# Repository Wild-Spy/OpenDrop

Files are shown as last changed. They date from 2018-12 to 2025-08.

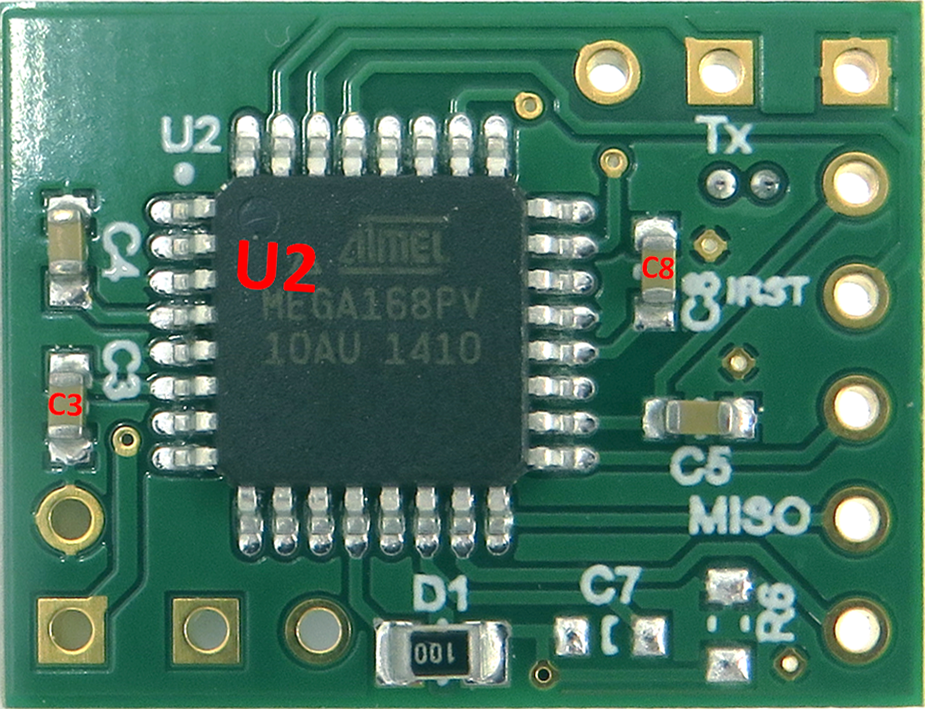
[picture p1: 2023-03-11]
Production/NichDrop Board V0.2 Production Files/Assisted Assembly Files/OpenDrop_PCB_Back.png

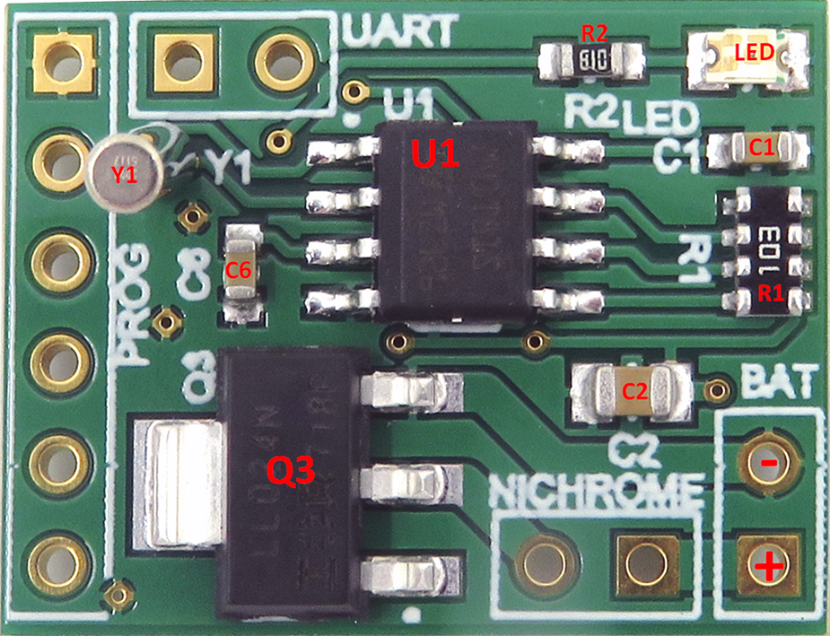
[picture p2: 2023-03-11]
Production/NichDrop Board V0.2 Production Files/Assisted Assembly Files/OpenDrop_PCB_Front.png

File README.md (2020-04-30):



# OpenDrop
OpenDrop is an open source, low cost drop-off unit for animal-borne devices. Provided herein is code for device firmware and programming software (Windows binaries available under [Releases](https://github.com/Wild-Spy/OpenDrop/releases)). Additionally, Gerber files for PCB fabrication and CAD files for a small/medium mammal housing mould master are included.

## Requirements
Device firmware is written in C and requires the AVR/Atmel Studio IDE - https://www.microchip.com/mplab/avr-support/avr-and-sam-downloads-archive

Programming software is written in Visual Basic and requires the Microsoft Visual Studio IDE - https://visualstudio.microsoft.com

## Further Information
A more detailed overview of OpenDrop and its use in wildlife biology is covered in: 

Rafiq, K., Appleby, R.G., Edgar, J.P., Jordan, N.R., Dexter, C.E., Jones, D.N., Blacker, A.R.F., and Cochrane, M. 2019, 'OpenDrop: An open-source, low-cost drop-off unit for animal borne devices', *Methods in Ecology and Evolution*, **10**, pp. 1517– 1522. https://doi.org/10.1111/2041-210X.13231

## License
This project is licensed under the terms of the GNU General Public License v3.0. See [LICENSE](LICENSE) for details.

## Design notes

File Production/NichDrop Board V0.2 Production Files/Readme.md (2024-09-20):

| Layer                	|  Filename             	|
|----------------------	|------------------------	|
| Top Copper          	|  NichromeDrop_V2R0.GTL 	|
| Top Solder Mask     	|  NichromeDrop_V2R0.GTS 	|
| Top Silk Screen     	|  NichromeDrop_V2R0.GTO 	|
| Bottom Copper       	|  NichromeDrop_V2R0.GBL 	|
| Bottom Solder Mask  	|  NichromeDrop_V2R0.GBS 	|
| Bottom Silk Screen  	|  NichromeDrop_V2R0.GBO 	|
| Board Outline       	|  NichromeDrop_V2R0.GKO 	|
| Top Solder Paste     	|  NichromeDrop_V2R0.GTP 	|
| Bottom Solder Paste  	|  NichromeDrop_V2R0.GBP 	|
| Excellon Drill File   |  NichromeDrop_V2R0.TXT 	|

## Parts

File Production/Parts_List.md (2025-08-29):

| **Designator** | **Side<sup>§</sup>** | **Size** | **Part**    | **Value** | **OI<sup>†</sup>** |
|:--------------:|:---------:|:--------:|:-----------:|:---------:|:-------:|
| U1             | Front     | ----     | ----        | M41T81S   | Yes     |
| R1             | Front     | ----     | ----        | 4xResNet  | No      |
| Q3             | Front     | SOT223   | MOSFET      | IRLL024N  | Yes     |
| C1             | Front     | 603      | Cap         | 0.1uF     | No      |
| C2             | Front     | 805      | Cap         | 47uF      | No      |
| C6             | Front     | 603      | Cap         | 0.1uF     | No      |
| R2             | Front     | 603      | Resistor    | 1kOhm     | No      |
| LED            | Front     | 805      | LED         | Red       | Yes     |
| Y1             | Front     | Can      | Xtal        | 32768Hz   | No      |
|                |           |          |             |           |         |
| U2             | Back      | ----     | ATMEGA168PV | ----      | Yes     |
| D1             | Back      | 0805     | Resistor    | 100hm     | No      |
| C3             | Back      | 0603     | Cap         | 0.1uF     | No      |
| C4             | Back      | 0603     | Cap         | 0.1uF     | No      |
| C5             | Back      | 0603     | Cap         | 0.1uF     | No      |
| C8             | Back      | 0603     | Cap         | 0.1uF     | No      |

<sup>§</sup> Side = Side of board<br>
<sup>†</sup> OI = Orientation Important

| **Part**          | **Qty** | **Designators**   | **Supplier** | **Supplier PN**       | **Description**             |
|:-----------------:|:-------:|:-----------------:|:------------:|:---------------------:|:---------------------------:|
| M41T81S           | 1       | U1                | Digikey      | 497\-4684\-1\-ND      | Timer                       |
| ATMEGA168PV       | 1       | U2                | Digikey      | ATMEGA168PV\-10AU\-ND | Microcontroller             |
| IRLL024N          | 1       | Q3                | Digikey      | IRLL024NPBFCT\-ND     | N Channel MOSFET            |
| C0805C473K5RACTU  | 1       | C2                | Digikey      | 399\-1166\-1\-ND      | 47uF 0805                   |
| TC164\-JR\-0710KL | 1       | R1                | Digikey      | TC164J\-10KCT\-ND     | 4x Resistor Network 10k     |
| CFS\-20632768EZBB | 1       | Y1                | Digikey      | 300\-8761\-ND         | 32\.768kHz Xtal in Can      |
| 150080RS75000     | 1       | LED               | Digikey      | 732\-4984\-1\-ND      | Red LED 0805                |
| 1K Resistor       | 1       | R2                | Element14    | RMCF0603JT1K00CT\-ND  | Any 1K 0603 Resistor        |
| 10R Resistor      | 1       | D1                | Element14    | RNCP0805FT010R0CT\-ND | Any 5% 0805 10R Resistor    |
| 0\.1uF Cap        | 6       | C1,C3,C4,C5,C6,C8 | \-\-\-\-     | 1276\-1112\-1\-ND     | 0\.1uF 0603 Decoupling Caps |

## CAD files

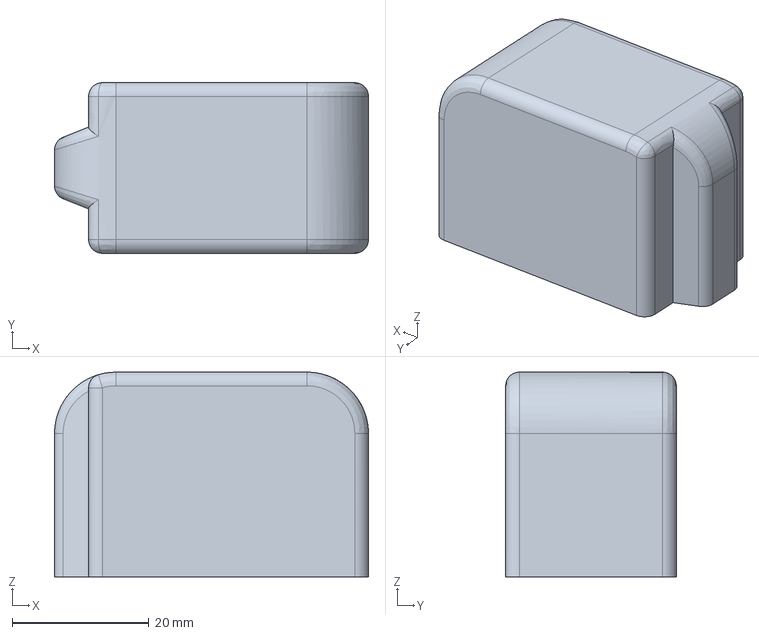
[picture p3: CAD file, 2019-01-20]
CAD_Files/OpenDrop_Mould_Master.stp
46.0 x 25.0 x 30.0 mm

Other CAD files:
CAD_Files/OpenDrop_Mould_Master.stl

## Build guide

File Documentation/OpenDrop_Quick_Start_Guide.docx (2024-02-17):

# OpenDrop Quick Start Guide

# Flashing the PCB Firmware

1. Download the programming files from: https://github.com/Wild-Spy/OpenDrop/tree/master/Code/Firmware/NichDrop/Debug
2. Download Atmel Studio 7 from: https://www.microchip.com/mplab/avr-support/avr-and-sam-downloads-archive
3. Observe the correct pinout on new PCBs (see below)
4. Connect pinout converter to ISP/PDI port on AVR Dragon (or alternative programmer such as Atmel ICE)
5. Connect programmer to PC and to the drop-off via the pinout converter
6. Drop-off must have power to program (i.e. be connected to a suitable 3.7-4.2V LiPo battery, both during firmware flashing and date/time programming). Remember, if the drop-off loses power during date/time programming it will not drop-off!
7. Battery power (+ve) on the drop-off is square (see red wire), and ground (-ve) is round (see black wire)
8. SPI connections are as follows: GND (ground) is square pin (also GND for UART), then VCC, Rst, SCK, MISO and MOSI

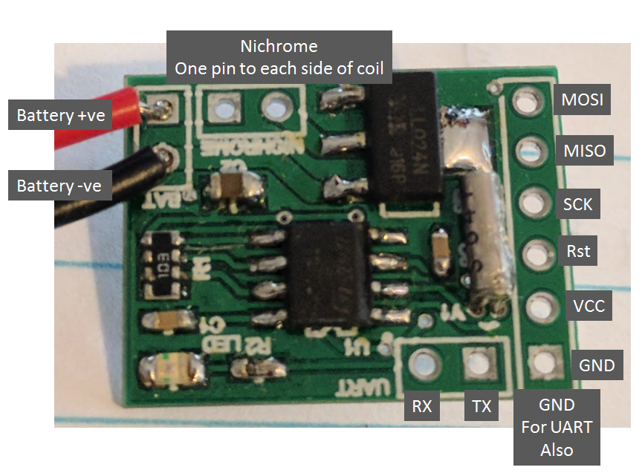
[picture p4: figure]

Drop-off PCB pinout overview

9. Open Atmel Studio 7
10. Open Tools -> Device Programming then choose:

Tool: Select your programmer from the dropdown (e.g. AVR Dragon)

Interface: ISP

Device: Atmega168p

Click the Apply button, then click the Read button. A device signature and target voltage (~3.3V) should appear. Then follow programming steps below.

Step 1. Load NichDrop_V1.1.0.hex in the Flash section of the Memories tab and click program.

Step 2. Load NichDrop_NORF_EEPROM_V1.0.eeprom in the EEPROM section of the Memories tab and click program.

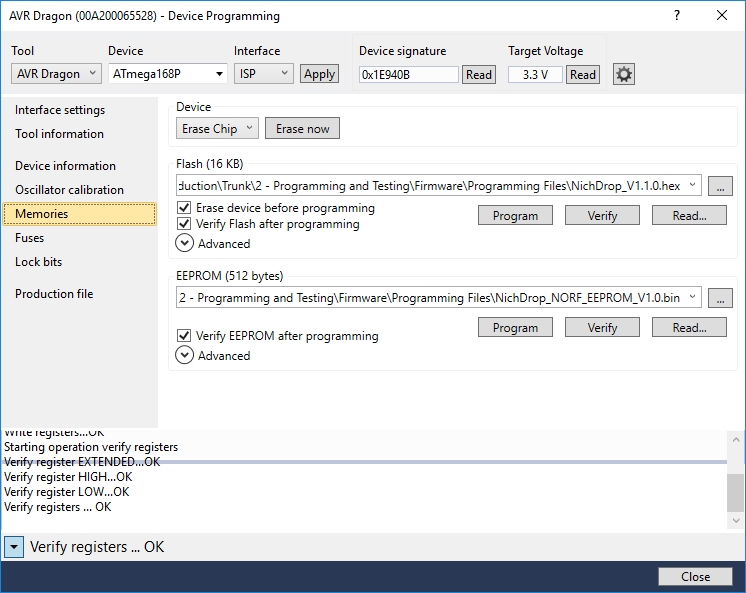
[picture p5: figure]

The Memories (i.e flash and EEPROM) tab in Atmel Studio 7

Step 3. On the Fuses tab, under the Fuses Register section, enter the following values:

Extended 0x01

High 0xDF

Low 0xE2

and click program.

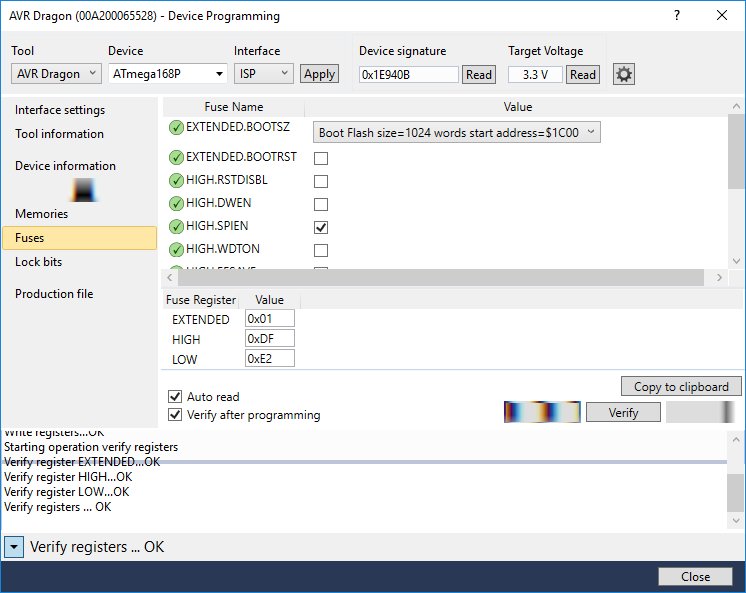
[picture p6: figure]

The Fuses tab in Atmel Studio 7

Note the settings for the ‘HIGH.BODLEVEL’ and ‘LOW.SUT_CKSEL’ parameters.

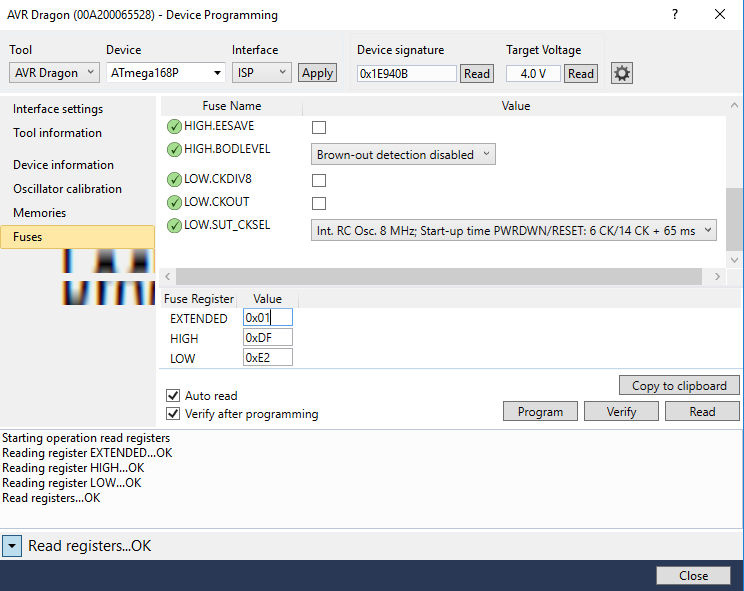
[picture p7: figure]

The Fuses tab in Atmel Studio 7

You can then unplug the programmer.

# Connecting to the Drop-Off

Once the firmware has been flashed, you can plug in a USB-to-Serial board and UART to program the drop-off’s time and date etc.

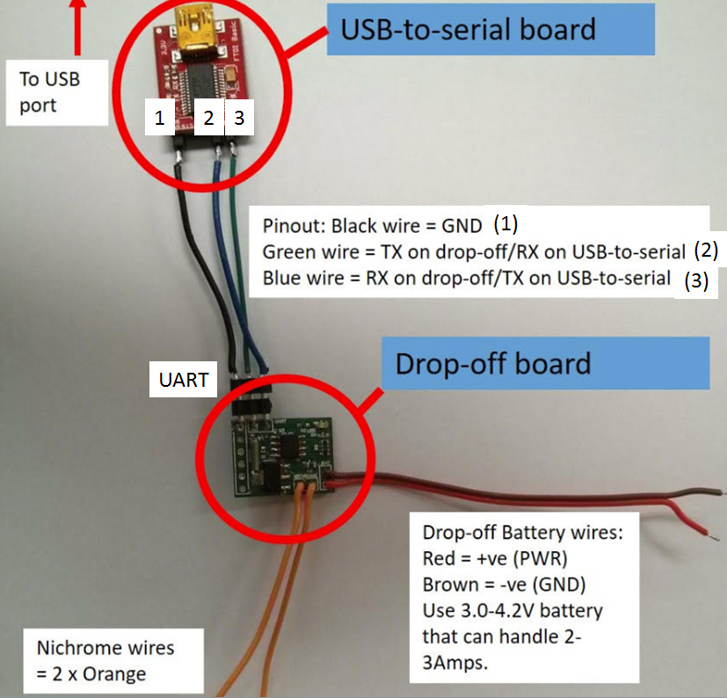
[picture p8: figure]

Drop-off PCB ready to be connected to PC via UART and USB-to-Serial breakout board

Once the USB-to-serial device has been assigned a virtual COM port, you can connect to the drop-off via the NichDropComms software (download from the repository’s Releases page). Use of the NichDropComms software is fairly straightforward. However, a PC running Windows with the .NET Framework 4 or later is required. You can download .NET installers from here: https://dotnet.microsoft.com/download/dotnet-framework.

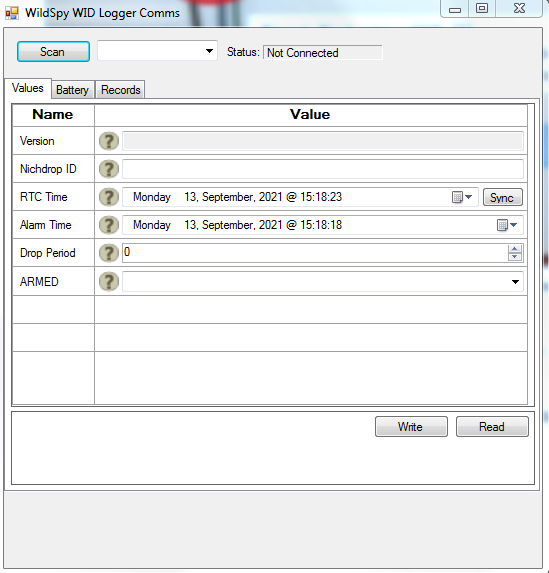
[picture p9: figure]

NichDropComms PC software (ignore incorrect title bar text)

# Turning the Drop-Off On

To power on a drop-off, a small, u-shaped jumper pin must be inserted into two of the three holes of the battery port.

CAUTION: Avoid incorrect pin installation as the device has no reverse polarity protection!

The correct pin ports are labeled with an upside down ‘U’, and correspond with the outside left (red dot) and middle holes with the drop-off oriented so the writing can be read normally.

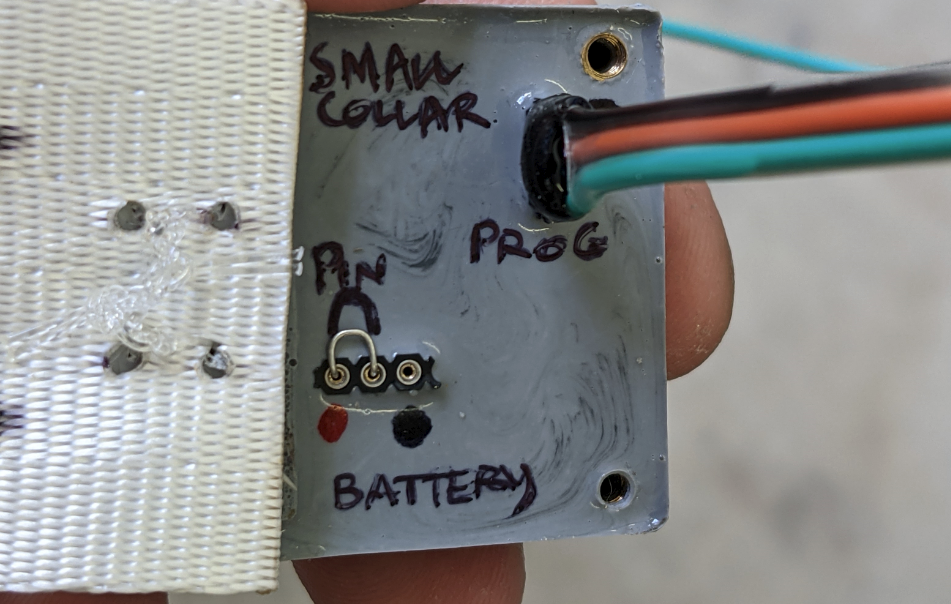
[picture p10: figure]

Drop-off with power pin and programming cable connected correctly

At all costs, avoid any electrical connection between the outside pins of the battery port (red and black spots) other than via the charging cable (see below) as these are the battery power and ground points respectively. The power pin must be inserted to program the drop-off.

# Programming the Drop-Off

The version of the software shown below may differ slightly to the most recent revision, but the ‘Values’ tab is essentially the same. Connect a drop-off to a computer with the installed and opened software, via the programming board and USB cables. Once connected, click, “Scan” on the software window, and then click the small drop down tab arrow in the nearby mini window (shown with a red circle and arrow respectively in figure 3). A long set of zeros (e.g. 00000000) should appear in the window beside the “Scan” button, and these must be selected by clicking on them, to initially populate the various parameter tabs shown with the green ticked circles ( ) in figure 3. If no numbers appear the drop-off has not been detected. Try unplugging both the cable and power pins, leaving everything disconnected for approximately 30-60sec and then trying again

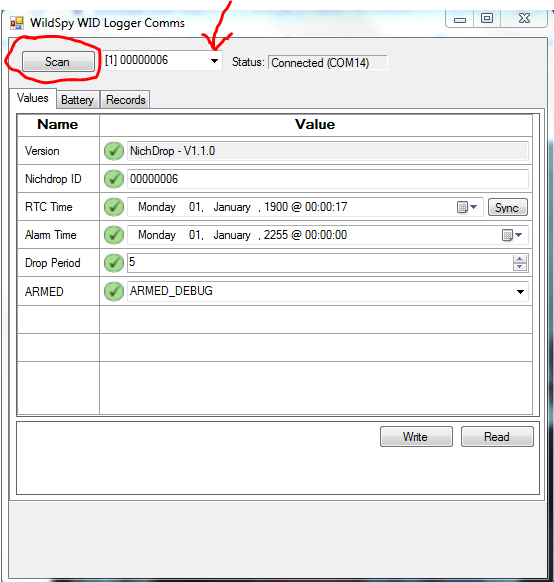
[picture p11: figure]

Drop-off window of the programming software showing a drop-off year far ahead in time

Before programming in any information, click the ‘Battery’ tab, and check to make sure the battery value is around 4.10-4.20 volts. Once the information is populated, you should see an ‘Alarm Time’ set to a point in the future (e.g. year 2222). If this is not the case, this should be the first thing you enter. Simply click on the year and change it to something like 2222 and then click the ‘Write’ button at the bottom of the window. This ensures that when you press ‘Sync’ you will not inadvertently activate the drop-off.

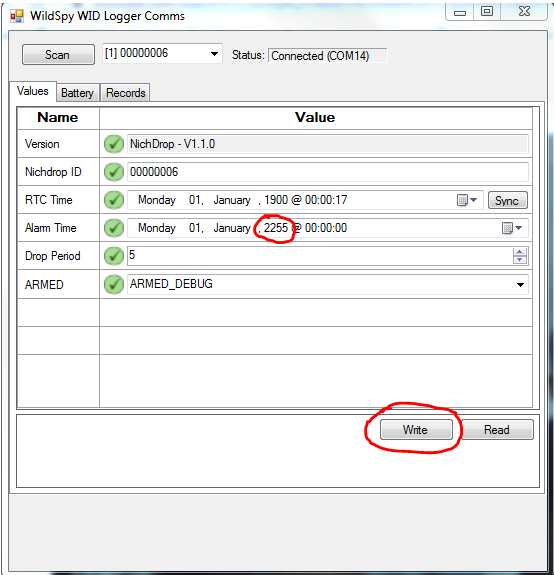
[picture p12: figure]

Alarm Time set to a point in the future

Once the ‘Alarm Time’ is set in advance of the current date, press ‘Sync’ to synchronize the current drop-off and PC times. Remember that whenever you change a setting you must also click write for it to take effect. Note also that any time a setting is changed but isn’t yet programmed, it will appear as an exclamation point with a yellow background, as opposed to a tick with a green background.

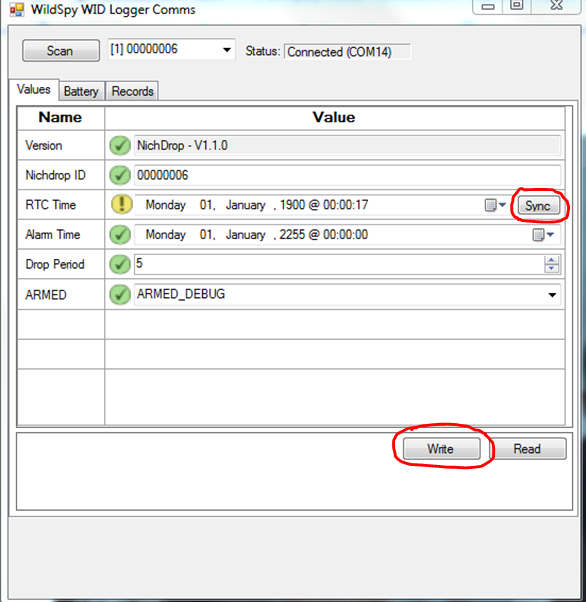
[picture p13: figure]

RTC current time/date setting

Once the time is correctly synced, you can program a preferred time and date for the drop-off to activate using the ‘Alarm Time’ setting. Click on the ‘Alarm Time’ year and change it to the current year. Then use the calendar drop down button to select a month and day. Finally, set the desired activation time. Once the ‘Alarm Time’ is correct, change the ‘ARMED’ setting to ‘ARMED_ON’. If you don’t, the drop-off will not activate.

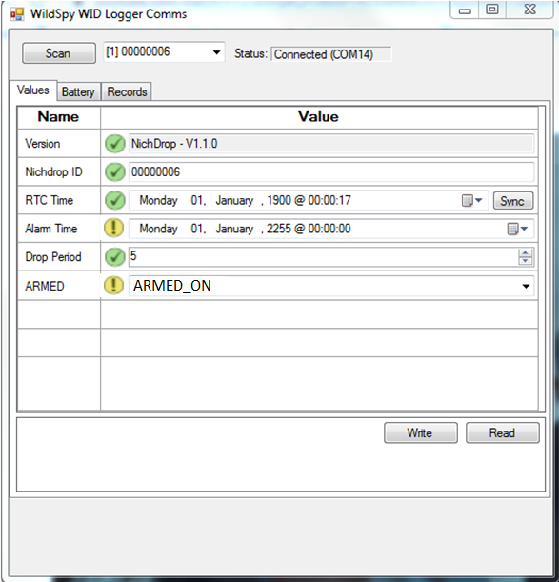
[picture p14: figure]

ARMED setting changes to ARMED_ON

The drop-off is programmed once Write is clicked (and all the exclamation marks will change to tick marks). The drop-off can then be unplugged from the cable.

# Making the Drop-Off Field-Ready

Once the drop-off is programmed, all the exposed battery and programming ports need to be covered in adhesive silicone/silicone putty, to ensure they are water resistant. Be careful not to get any silicone on the nylon line or the section of collar material the line is attached to because this might hamper or even prevent a clean detachment. The putty takes about 30min to not be tacky anymore, as do most adhesive silicones, but it usually takes at least 24 hours for them to fully cure. Avoid any heat source (e.g. heat gun) getting close to the nylon line as this might damage or melt it.

Notes and Troubleshooting

The drop-off activation process involves a heating element (nichrome wire) getting hot enough to melt nylon line that attaches the drop-off to the collar material. CAUTION: This wire reaches temperatures of multi-hundred degrees centigrade and should never be touched during activation! In a complete drop-off, this entire section is typically sealed off behind a 3mm acrylic plate. Regardless, it’s advisable to keep fingers away from this section when the drop-off is in activation mode. A drop-off is set by default to activate approximately five times over a few minutes to ensure it has completely detached a collar, so it’s possible you might pick it up during this activation period if you are present when it starts and the collar detaches from an animal. On the animal there should be an additional layer of collar material between it and the underside of the drop-off. That way almost no heat should be detectable by the animal and it won’t be harmed.

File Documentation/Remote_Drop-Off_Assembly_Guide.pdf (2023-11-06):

A (rough) Guide to Building a DIY Remote-controlled Drop-off (draft)

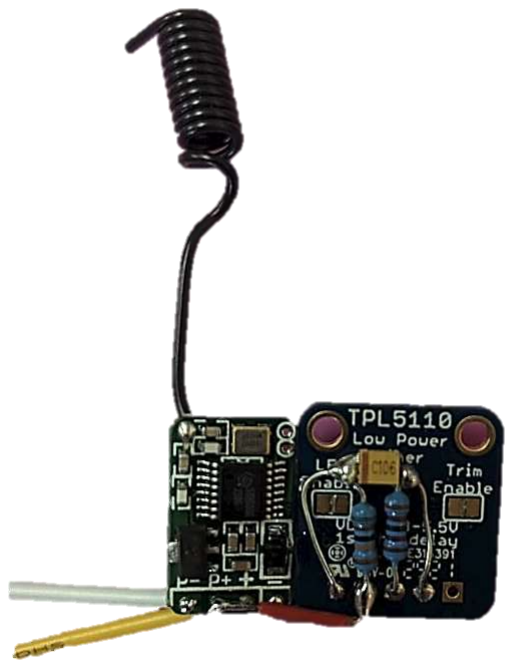
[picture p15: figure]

# A warning up front. Nichrome can get red hot when a current is applied so please be very careful when testing or assembling devices that use nichrome. Also, be careful with lithium polymer batteries as they are highly energetic if the +ve and –ve terminals are accidentally

connected, or the cell is damaged.

Description
This remote controlled detachment system uses simple, off-the-shelf components to provide a flexible, low cost and low-moderate difficulty option for animal-borne devices. It is built around two boards: A TPL5110 from Adafruit, and a 433MHz remote ‘switch’ board from Aliexpress. Additionally, three passive components – two resistors and a capacitor control all functionality. Any single cell (3.7V nominal) lithium polymer (lipo) ‘battery’ capable of handling about two amperes of current draw (dependent upon the configuration and gauge of the nichrome element used to heat and sever nylon attachment line) is suitable for use. Below, a complete description and set of instructions is given on how to assemble the system (with the exception of ‘housing’ or encapsulation, which can be covered upon request).

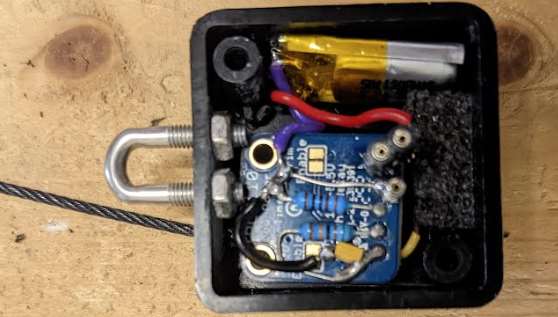
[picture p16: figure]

An example of the detachment system assembled into an offthe-shelf enclosure
(https (https://www.altronics.com.au/p/h9010-hammond-35lx35wx20hmm-mini-flange-mount-abs-box/)://www.altronics.com.au/p /h9010 (https://www.altronics.com.au/p/h9010-hammond-35lx35wx20hmm-mini-flange-mount-abs-box/)- (https://www.altronics.com.au/p/h9010-hammond-35lx35wx20hmm-mini-flange-mount-abs-box/)hammond (https://www.altronics.com.au/p/h9010-hammond-35lx35wx20hmm-mini-flange-mount-abs-box/)-35lx35wx20hmm (https://www.altronics.com.au/p/h9010-hammond-35lx35wx20hmm-mini-flange-mount-abs-box/)- (https://www.altronics.com.au/p/h9010-hammond-35lx35wx20hmm-mini-flange-mount-abs-box/)mini (https://www.altronics.com.au/p/h9010-hammond-35lx35wx20hmm-mini-flange-mount-abs-box/)- (https://www.altronics.com.au/p/h9010-hammond-35lx35wx20hmm-mini-flange-mount-abs-box/)flange (https://www.altronics.com.au/p/h9010-hammond-35lx35wx20hmm-mini-flange-mount-abs-box/)-mount (https://www.altronics.com.au/p/h9010-hammond-35lx35wx20hmm-mini-flange-mount-abs-box/)- (https://www.altronics.com.au/p/h9010-hammond-35lx35wx20hmm-mini-flange-mount-abs-box/)abs (https://www.altronics.com.au/p/h9010-hammond-35lx35wx20hmm-mini-flange-mount-abs-box/)- (https://www.altronics.com.au/p/h9010-hammond-35lx35wx20hmm-mini-flange-mount-abs-box/)box (https://www.altronics.com.au/p/h9010-hammond-35lx35wx20hmm-mini-flange-mount-abs-box/)/). (https://www.altronics.com.au/p/h9010-hammond-35lx35wx20hmm-mini-flange-mount-abs-box/) Lid not shown. Nichrome element is hidden under a section of foam on the right-hand-side of the case

The TPL5110 board from Adafruit (https://www.adafruit.com/product/3435
) is described as a: “...a stand-alone breakout that will turn any electronics into low-power electronics! It will take care of turning your project on/off using a built in timer that can vary from once every 100ms up to once every two hours. Basically, the TPL will turn on periodically, adjustable by potentiometer or resistor, and turn on your project's power. It will then wait until a signal is received from the project to tell the TPL that it can safely turn off the power.”

For the purposes of building a remote controlled device detachment system, we use the TPL5110 to control two, associated procedures: how long the device is awake and listening for a signal from the user to activate detachment, and, how long it should be asleep in between these wake up intervals. The maximum sleep interval possible is two hours, meaning that, if you wanted, you could have a device only wake up once every two hours to listen for signal (not advisable, but would definitely save a lot of power).

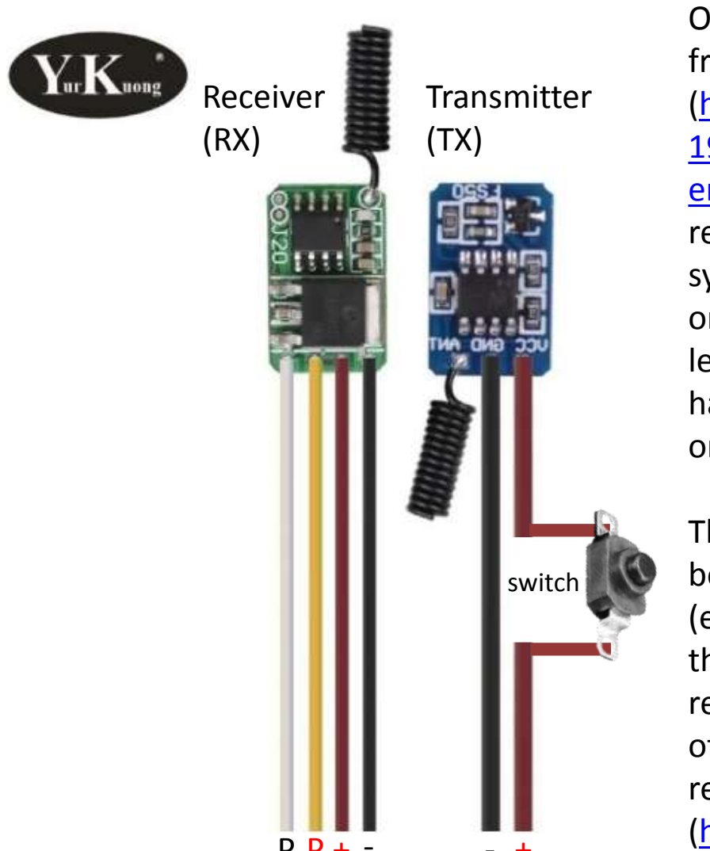
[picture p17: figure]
Receiver (RX); Transmitter (TX); switch

One option for a remote switch is a board from Aliexpress supplier YurKuong (https (https://www.aliexpress.com/item/1005003198881091.html)://www.aliexpress.com/item/1005003 198881091.html?spm=a2g0o.order_list.ord er_list_main.97.34941802Z5uhHc). (https://www.aliexpress.com/item/1005003198881091.html) Both a receiver and transmitter are required for the system to operate, with the receiver shown on the left-hand-side of the image to the left, whilst the transmitter is on the righthand-side. Choose the ‘momentary’ option on the web store.

There are options for up to 12 receiver boards being controlled by a single remote (e.g. https://tinyurl.com/yrswk4je) but note, these require individual pairing between the receivers and the remote buttons. Bundles of a single remote pre-paired with four receiver boards are also available (https://tinyurl.com/2s3t6hft).
Some testing might be required to ensure the same transmitter doesn’t activate multiple receivers, in case this could be a problem in the field.
+ - | - +
P
+

P
-}

to nichrome
wires

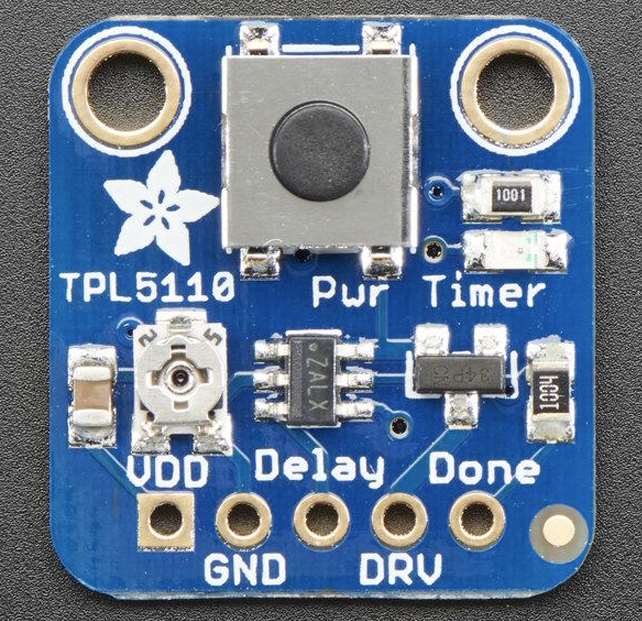
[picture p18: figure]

In order to control the timing of the TPL5110, three additional, passive components are required, along with some slight modification to the TPL5110 board itself.

The sleep delay period only requires a single resistor to be joined between the ‘Delay’ and ‘GND’ pads. Resistor values dictate the length of the sleep delay and range from: 5.2kohm for a one second delay, to 170kohm for a two hour delay. Probably the most likely sleep intervals for the detachment receiver are between one minute (22.0kohm) and ten minutes (57.44kohm). This is because the system is quite ‘dumb’ and requires that the transmitter signal be sent as soon as it wakes up. Thus, if it only wakes up every 10 minutes, the transmitter has to be on and sending signal constantly for this period to safely be received.

A full selection of possible resistor values can be found in the Adafruit ‘Usage’ page for the board (https://learn.adafruit.com/adafruit-tpl5110-power (https://learn.adafruit.com/adafruit-tpl5110-power-timer-breakout/usage)- (https://learn.adafruit.com/adafruit-tpl5110-power-timer-breakout/usage)timer (https://learn.adafruit.com/adafruit-tpl5110-power-timer-breakout/usage)- (https://learn.adafruit.com/adafruit-tpl5110-power-timer-breakout/usage)breakout/usage). (https://learn.adafruit.com/adafruit-tpl5110-power-timer-breakout/usage)

The ‘awake’ period is controlled using a simple resistor-capacitor circuit, joined between the ‘DRV’ and ‘Done’ pads, as well as a ground connection (e.g. ‘GND’ on the TPL5110 board).

A simple schematic, showing the circuit is as follows:

In this schematic, a resistor is joined between the ‘DRV’ and ‘Done’ pads. The capacitor is joined in between the connection to the ‘Done’ pad, with the other side going to ‘GND’. Values of both the resistor and the capacitor together set the ‘awake’ interval. The equation for this is:
where is ‘tau’ or the interval in seconds
R is the value of the resistor in ohms
C is the value of the capacitor in Farads
An example is 500kohms (500000 ohms) x 10uF (0.00001 farads) = 5 seconds
A calculator can be found here: https://www.digikey.com.au/en/resources/conversioncalculators/conversion (https://www.digikey.com.au/en/resources/conversion-calculators/conversion-calculator-time-constant)- (https://www.digikey.com.au/en/resources/conversion-calculators/conversion-calculator-time-constant)calculator (https://www.digikey.com.au/en/resources/conversion-calculators/conversion-calculator-time-constant)- (https://www.digikey.com.au/en/resources/conversion-calculators/conversion-calculator-time-constant)time (https://www.digikey.com.au/en/resources/conversion-calculators/conversion-calculator-time-constant)- (https://www.digikey.com.au/en/resources/conversion-calculators/conversion-calculator-time-constant)constant (https://www.digikey.com.au/en/resources/conversion-calculators/conversion-calculator-time-constant) using a battery voltage of 3.7 - 4.2V (lipo).

R

C

GND

DRV | Done

e.g. 500 k
| e.g. 10 uF

+ve battery

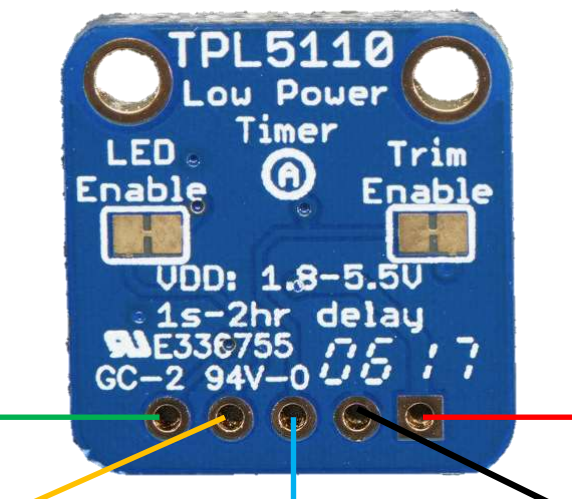
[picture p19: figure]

-ve battery
-ve receiver
Delay resistor leg
R-C capacitor

R-C resistor leg

Delay (sleep)
resistor leg R-C resistor leg (to capacitor)
+ve receiver

The various connections for the TPL5110 board

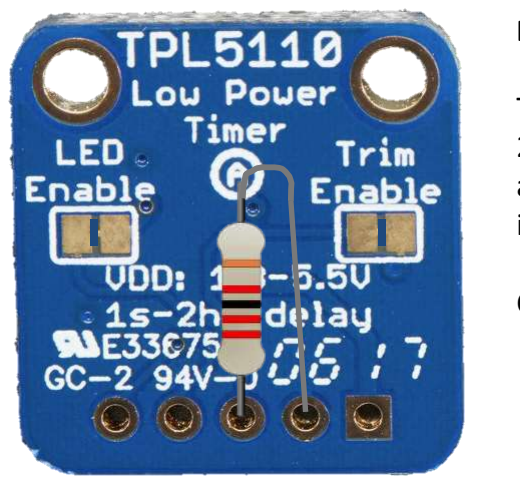
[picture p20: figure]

Delay or ‘sleep’ interval

TPL5110 board shown with a stylised version of a 22kohm resistor soldered between the ‘Delay’ and ‘GND’ pads – this would equate to a sleep interval of approximately 1 minute.

Components are not to scale

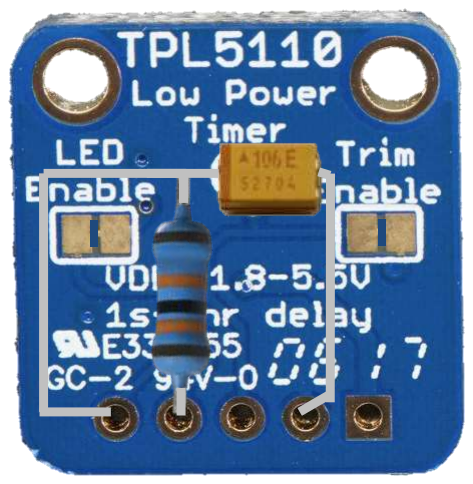
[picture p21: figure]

‘Awake’ interval using an R-C circuit

Resistor-capacitor (R-C) circuit shown here with a 500 kohm resistor (or 510k if 500k can’t be found) joined to the ‘DRV’ and ‘Done’ pads. In between this connection (i.e. same leg of the resistor going to the ‘Done’ pad), the +ve side of the capacitor (in this case, marked with a vertical ‘stripe’ on a 10uF tantalum capacitor) is attached, whilst the –ve side of the capacitor (i.e. no ‘stripe’) is joined to the ‘GND’ pad.

In this arrangement, an ‘awake’ interval of approximately five seconds will be produced once the TPL5110 board wakes from it’s sleep interval. This means the receiver board is awake and listening for a transmitter signal for approximately five seconds (in practice, interval may vary a bit).

Again, components are not to scale

An assembled TPL5110 board. Note that the –ve side of the capacitor has been soldered to the ‘Delay’ resistor leg that is going to ‘GND’, whilst the +ve side of the capacitor is soldered to the leg of the ‘DRV’ resistor going to ‘Done’. More on the capacitor polarity a few pages below

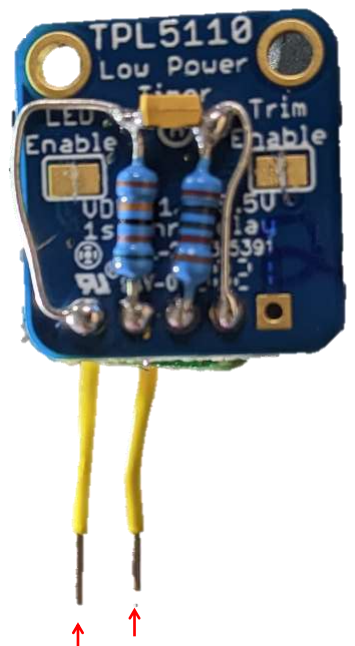
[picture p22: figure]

Nichrome element wires (coming from P- and P+ on the unseen receiver board)

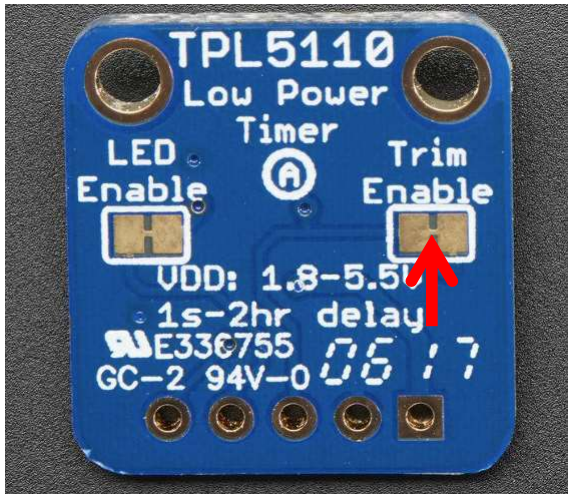
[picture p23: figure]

In order to use the ‘Delay’ resistor as outlined above, you’ll need to sever the small, copper trace joining the pads under the ‘Trim Enable’ label (see red arrow on picture to the left).

The ‘LED Enable’ pads can also be severed to save even more power, but should be done only after initial tests to ensure troubleshooting can be easily achieved.

And you can always solder the pads on each back together if required

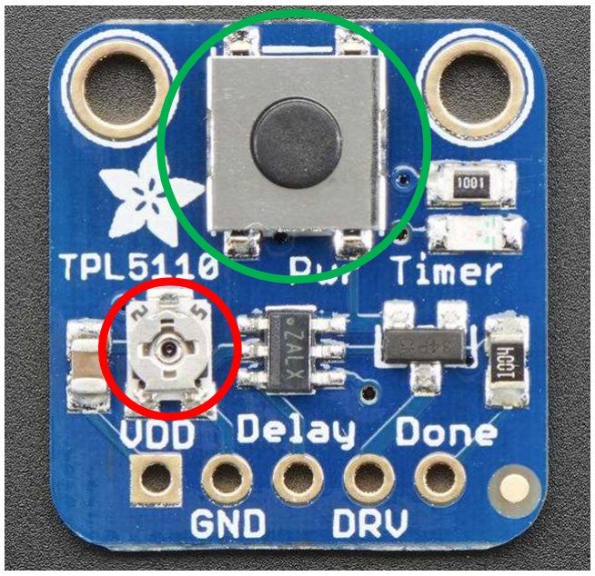
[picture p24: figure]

The pushbutton switch (circled in green) can be used in initial tests to ensure the system is working. When it is pushed, the TPL5110 wakes up immediately, regardless of the resistor value setting. Be careful you do not accidentally press this switch in a unit about to be deployed, as it will immediately detach. If you want to disable the switch after initial testing, cut each of the four legs attaching it to the board with a side cutter and remove it (and make sure the battery is not connected). Alternatively, desolder it from the board.

The board also has a ‘trimpot’ or variable resistor already attached (circled in red), but it can be difficult to accurately set. I’ve found it’s best to disable this (severing the ‘Trim Enable’ pads) and use a set resistor. It doesn’t need to be removed as long as the ‘Trim Enable’ pads have been separated (see previous page)

+

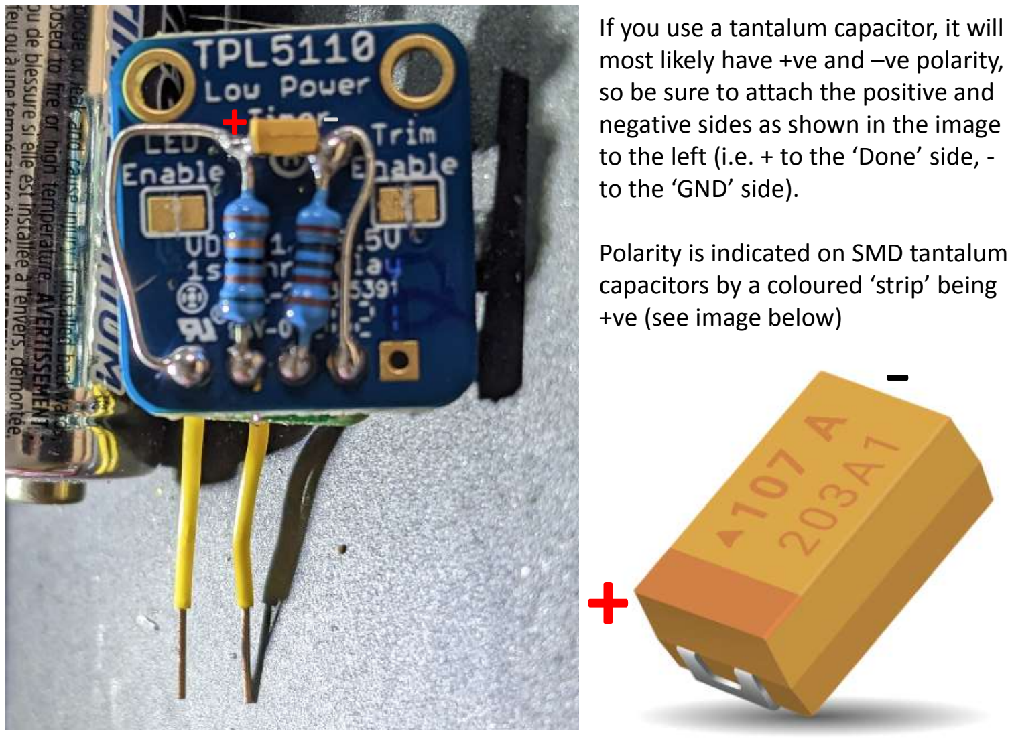
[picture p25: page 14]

If you use a tantalum capacitor, it will most likely have +ve and –ve polarity, so be sure to attach the positive and negative sides as shown in the image to the left (i.e. + to the ‘Done’ side, -to the ‘GND’ side).

Polarity is indicated on SMD tantalum capacitors by a coloured ‘strip’ being +ve (see image below)

+

Once the TPL5110 board has been prepared, you can join it to the receiver board. In order to make it easier to see, I’ve used a ‘clean’ version of the TPL5110 board in the image to the left, so only the connections to the receiver board are clearly visible. In reality, the system will only work with a fully assembled TPL5110 (i.e. all components are attached).

Connect the ‘DRV’ pad on the TPL5110 board to the ‘+’ pad on the receiver board.

Connect the ‘GND’ pad on the TPL5110 board to the ‘-’ pad (not P-) on the receiver board. Alternatively, you can connect the ‘-’ pad on the receiver board directly to the battery –ve if it’s easier.

The yellow and white wires shown on the receiver board connect to the nichrome element

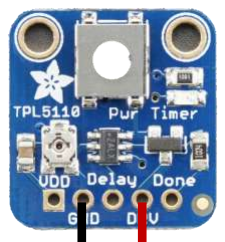
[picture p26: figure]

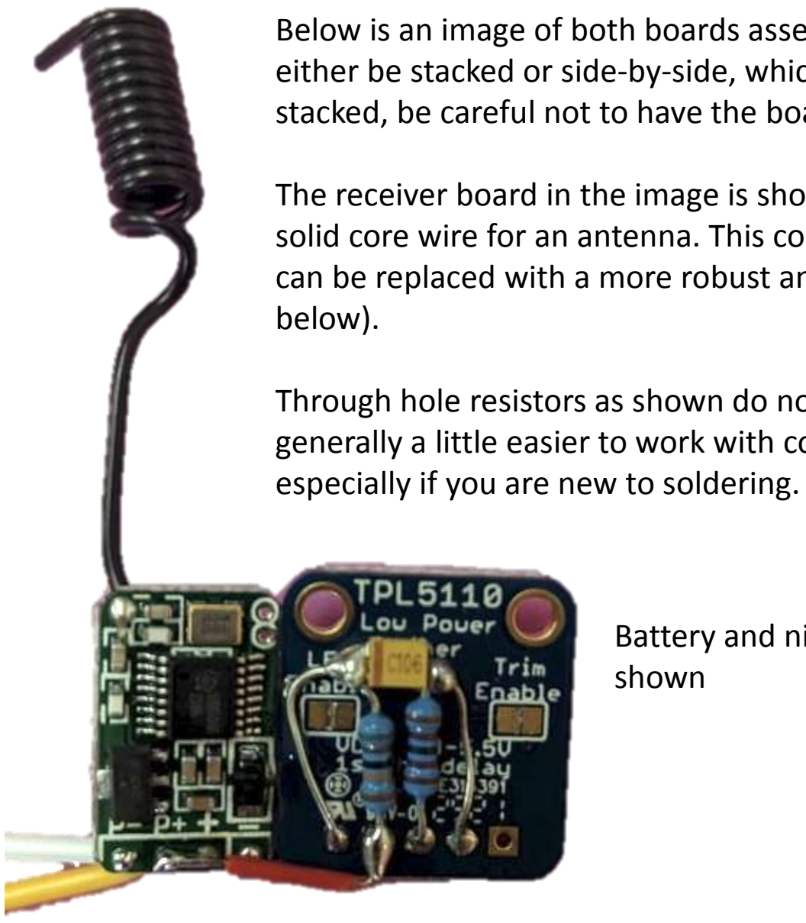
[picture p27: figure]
below).; especially if you are new to soldering.

Battery and nichrome element connections are not shown

Below is an image of both boards assembled together. The boards can either be stacked or side-by-side, whichever best suits your application. If stacked, be careful not to have the boards touch.

The receiver board in the image is shown with a coiled section of black, solid core wire for an antenna. This comes from the factory like this, but can be replaced with a more robust antenna if required (see pages

Through hole resistors as shown do not have to be used although they are generally a little easier to work with compared to SMD resistors,

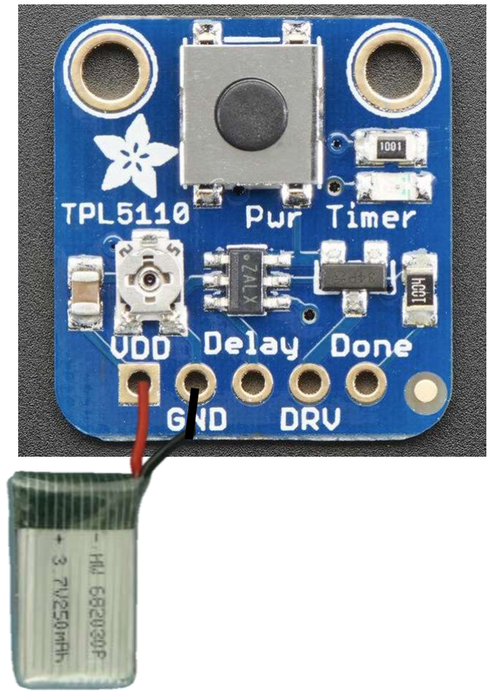
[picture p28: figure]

Battery
Join the +ve wire (usually red) of the battery to the ‘VDD’ pad and the –ve wire (usually black) of the battery to the ‘GND’ pad on the TPL5110. Note however that there is no way to charge the battery if it is joined directly to the board (i.e. you could damage one or both boards if you attempt to charge a battery whilst it is connected).

Alternatively, wire in a battery connector so the battery can be unplugged and recharged. If you plan on encapsulating everything and won’t have access to the battery, contact me to discuss options, which will usually involve something like an exposed, intermediate connection/disconnection point on one wire (usually +ve) that can be bridged to establish a connection, and an exposed point of contact to the other wire, so that a charger can be safely attached without the battery being connected to the boards. An example can be found below

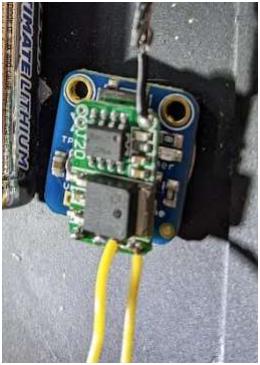
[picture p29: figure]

The nichrome element wires (shown in the image as yellow wires) are connected on the receiver board to the p+(ve) and the p-(ve) pads (noting that the p-ve is different from the ‘plain’ -(ve) or ground pad). On this particular receiver switch board, the ‘p+’ and ‘+’ pads are joined together so one nichrome element wire can be connected to either of these, but it’s usually easiest to connect it to the ‘p+’ wire that’s already soldered in place. If the wires from the factory look a bit dodgy though, you can of course replace them all.

The black wire coming from the top of the board is part of a replacement antenna I’ve attached to the antenna connection on the board. Some form of environmentally protected, flexible, strong wire is recommended as an external antenna on all devices, so that range is maximised (examples are given in a future slide and in the Bill of Materials at the end of the guide).

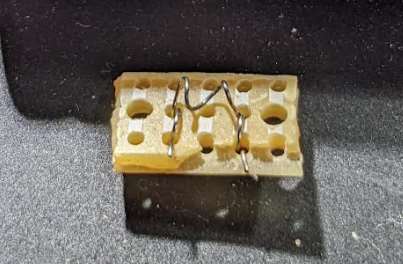
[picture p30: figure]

The nichrome element itself usually consists of about 2 or more ‘coils’ of nichrome wire, with each end section then connected to the wires from the receiver board. Nichrome comes in many gauges, but generally, you’ll likely want to use something around 28-34 AWG. The smaller the number, the thicker the wire, and the more current that is needed to generate heat. Thicker wire is more easily worked with, but I’d recommend the thinnest wire you can reliably work with. I usually coil nichrome around a stretched out, large paper clip.

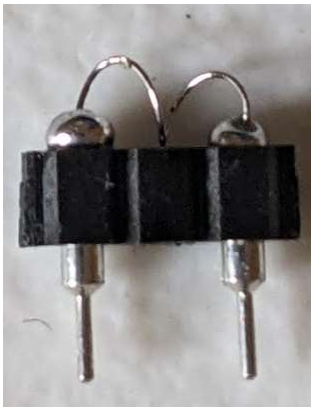
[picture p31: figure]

For very small devices (i.e. small, low capacity batteries), 34 AWG is probably best, and you may need to experiment with lengths and coil sizes to make sure it can heat up enough to melt nylon.

One recent tip from a WILDLABS community member is to use dyneema line instead of normal nylon fishing line, as it has a lower melting point (but is still very strong), so not as much current is needed to sever it.

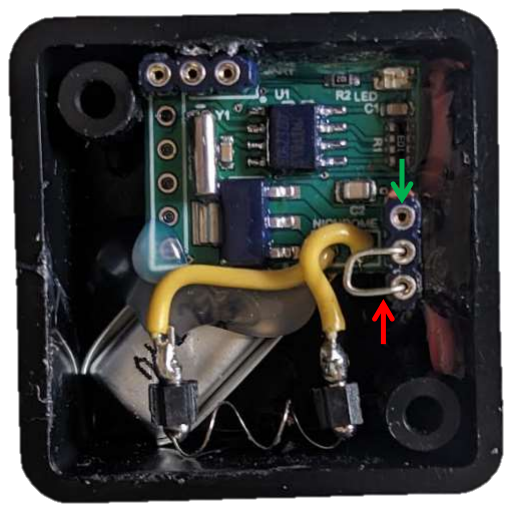
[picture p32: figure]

I don’t have a very good picture of the nichrome element attached to the ‘p+’ and ‘p-’ wires of the receiver board, but I do have this image of the same attachment for our timer drop-off board.

On this timer board version, I used machine headers to attach the nichrome coil. These were then attached to the nichrome element wires (yellow).

You can also see an example of an ‘intermediate’ battery connection (red arrow) using machine headers, where the ‘u-shaped’ pin (a section of resistor leg stuck into the header sockets) joins the battery to the board. When this pin is removed, the battery can be safely charged via the machine header directly connected to the battery (outer socket) and the ground machine header socket (green arrow) as it is no longer electrically connected to the board

The nylon line is either placed through the inside of the nichrome coils or over them in such a way that they contact or are very close to the nichrome, then exits the enclosure, ready to be tied onto the collar. When the nichrome heats up, the nylon melts and slips through the enclosure, releasing the collar or device from the animal.

Multiple nylon lines can be used to strengthen the attachment, as can thicker nylon. The ‘strength’ ratings on most nylon fishing lines equate to a straight section of line under strain. An approximate rule-of-thumb is that a tied section of line has half the breaking strength of a straight section. Thus, if you want a 20kg breaking strain you can either use a 40kg rated line (which will usually require a decently thick gauge of nichrome, such as 28 or 30 AWG), or, two sections of 20kg line. Make sure that if you use multiple sections of line, they do not overlap inside the coil, or they might snag during detachment.

Extensive testing is recommended for any designs, especially as this is a prototype without much field testing. Range is estimated to be about 250-500 m line-of-sight, although this could potentially be extended by using a directional (e.g. Yagi) antenna on the transmitter. For the receiver antenna, I recommend some type of environmentally protected, flexible wire (e.g. https://www.bcf.com.au/p/surecatch-nylon-coated-trace-wire-10m-clear-90lb/112489.html) cut to a quarter of one wavelength (~17.31 cm). It can be difficult to solder to stainless steel, so protected galvanised wire is probably ok for most terrestrial environments. I’ve found lead-free solder often ‘tins’ galvanised wire, especially if flux is used. The same is true for nichrome (solder doesn’t tend to stick to it) so consider using a mechanical (e.g. crimp) to attach something that can be soldered too (see next page).

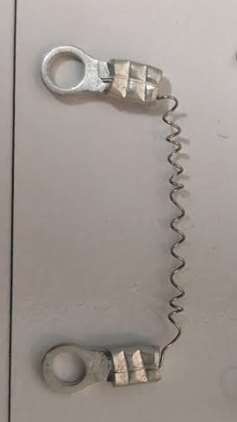
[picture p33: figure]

A coiled section of 28 AWG nichrome as used in the ‘Sensordrop’
(https://onlinelibrary.wiley.com/doi/full/10.1002/ece3 .10220). (https://onlinelibrary.wiley.com/doi/full/10.1002/ece3.10220) Two ‘ring crimps’ (https://www.altronics.com.au/p/h1520b-3.7mmuninsulated (https://www.altronics.com.au/p/h1520b-3.7mm-uninsulated-ring-terminal-crimp-pk-10/)- (https://www.altronics.com.au/p/h1520b-3.7mm-uninsulated-ring-terminal-crimp-pk-10/)ring (https://www.altronics.com.au/p/h1520b-3.7mm-uninsulated-ring-terminal-crimp-pk-10/)- (https://www.altronics.com.au/p/h1520b-3.7mm-uninsulated-ring-terminal-crimp-pk-10/)terminal (https://www.altronics.com.au/p/h1520b-3.7mm-uninsulated-ring-terminal-crimp-pk-10/)- (https://www.altronics.com.au/p/h1520b-3.7mm-uninsulated-ring-terminal-crimp-pk-10/)crimp (https://www.altronics.com.au/p/h1520b-3.7mm-uninsulated-ring-terminal-crimp-pk-10/)- (https://www.altronics.com.au/p/h1520b-3.7mm-uninsulated-ring-terminal-crimp-pk-10/)pk (https://www.altronics.com.au/p/h1520b-3.7mm-uninsulated-ring-terminal-crimp-pk-10/)- (https://www.altronics.com.au/p/h1520b-3.7mm-uninsulated-ring-terminal-crimp-pk-10/)10 (https://www.altronics.com.au/p/h1520b-3.7mm-uninsulated-ring-terminal-crimp-pk-10/)/) (https://www.altronics.com.au/p/h1520b-3.7mm-uninsulated-ring-terminal-crimp-pk-10/) were used to mechanically attach to the nichrome. For small devices, long lengths of nichrome consisting of many coils are not necessary.

As previously mentioned, an alternative approach is to use machine headers (e.g.
https://www.altronics.com.au/p/p5400-oupiin-40-way (https://www.altronics.com.au/p/p5400-oupiin-40-way-machined-pin-pcb-socket/)- (https://www.altronics.com.au/p/p5400-oupiin-40-way-machined-pin-pcb-socket/)machined (https://www.altronics.com.au/p/p5400-oupiin-40-way-machined-pin-pcb-socket/)- (https://www.altronics.com.au/p/p5400-oupiin-40-way-machined-pin-pcb-socket/)pin (https://www.altronics.com.au/p/p5400-oupiin-40-way-machined-pin-pcb-socket/)- (https://www.altronics.com.au/p/p5400-oupiin-40-way-machined-pin-pcb-socket/)pcb (https://www.altronics.com.au/p/p5400-oupiin-40-way-machined-pin-pcb-socket/)- (https://www.altronics.com.au/p/p5400-oupiin-40-way-machined-pin-pcb-socket/)socket (https://www.altronics.com.au/p/p5400-oupiin-40-way-machined-pin-pcb-socket/)/), (https://www.altronics.com.au/p/p5400-oupiin-40-way-machined-pin-pcb-socket/) as there are usually fairly good at retaining nichrome as long a blob of solder is placed over the socket once the nichrome has been inserted. Again, lead-free solder seems to be a little better for this

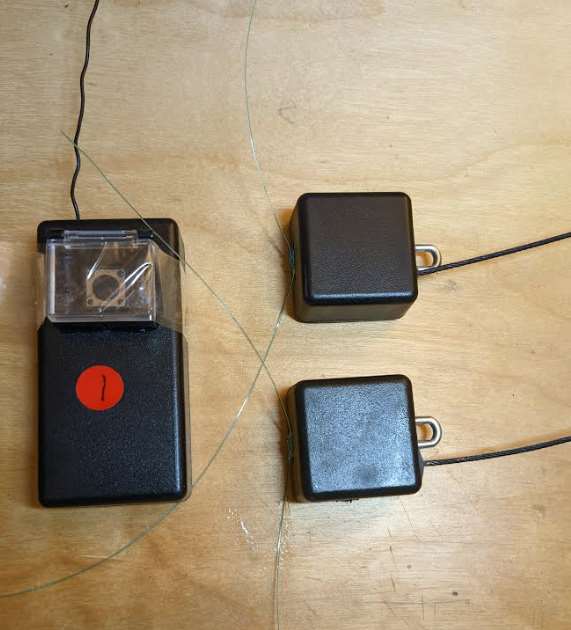
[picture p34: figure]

Two, fully assembled remote drop-offs inside off-the-shelf enclosures, along with a
remote (transmitter – red
sticker labelled ‘1’). Note the nylon line that, in this case, has been pre-knotted and tied to the front side of the enclosure. The nylon can either exit the front or underside depending on the application. The metal u-bolts visible on the far righthand-side of each drop-off unit are for permanently attaching to a collar. This way, the nylon side of the collar separates during attachment, but the drop-off stays attached to the collar as it falls away. A variety of attachment methods are
possible, but usually involve bolting or screwing an
enclosure to a collar in some way.

Bill of Materials

Item | Unit Number | Unit Cost (USD)* | Total Cost (USD)* | Link
Adafruit TPL5110 low power timer board | 1 | $4.95 | $4.95 https://www.adafruit.com/product/3435
YurKuong 433 Mhz receiver switch board | 1 | $5.20 | $5.20 https://www.aliexpress.com/item/1005003198881091.html?spm=a2g0o.order_list.order_list_main.97.34941802Z5uhHc
YurKuong 433 Mhz transmitter board | 1 | $5.20 | $5.20 https://www.aliexpress.com/item/1005003198881091.html?spm=a2g0o.order_list.order_list_main.97.34941802Z5uhHc
250mAh 3.7V 20C lipo battery | 1 | $5.71 | $5.71 https://ecocell.com.au/product/lipo-hp-250-552525/
Length of coiled 32 AWG nichrome | 1 | $0.20 | $0.20 https://www.amazon.com.au/Nichrome-80-250-Gauge-Resistance-Wire/dp/B07CJ63YYT?ref_=v_sp_product_dpx
Machine headers | 4 | $0.10 | $0.40 https://www.altronics.com.au/p/p5400a-40-way-machined-pin-pcb-socket/
0.5mm solid core wire | 6 | $0.10 | $0.60 https://www.altronics.com.au/p/w2430-solid-core-0.5mm-6-colour-hobby-wire-pack/
22.0Kohm resistor | 1 | $0.10 | $0.10 https://www.altronics.com.au/p/r7590-22k-0.25w-metal-film-resistor-pk-10/
510kohm resistor | 1 | $0.10 | $0.10 https://www.altronics.com.au/p/r7623-510k-0.25w-metal-film-resistor-pk-10/
10uF capacitor | 1 | $0.50 | $0.50https://www.altronics.com.au/p/r9189a-10uf-16v-smd-tantalum-capacitor-pk-10/
Switch (for transmitter) | 1 | $2.50 | $2.50 https://www.altronics.com.au/p/s1082a-spst-alternate-black-solder-tail-pushbutton-switch/
Receiver antenna wire 1/4 wave (17.31cm) | 2 | $0.10 | $0.20 https://www.bcf.com.au/p/surecatch-nylon-coated-trace-wire-10m-clear-90lb/112489.html
Total | $25.66

*cost does not include shipping or taxes

*all costs are estimated

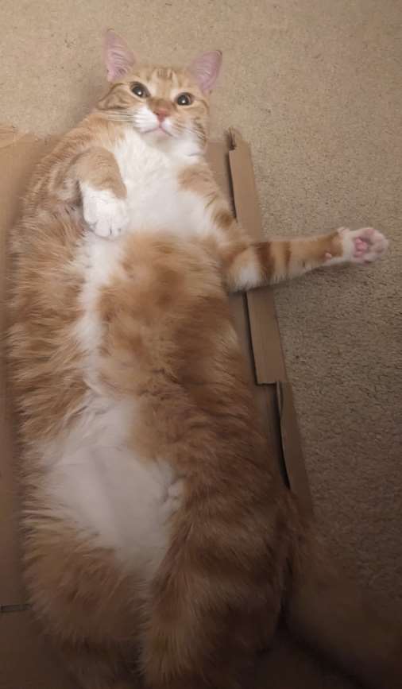
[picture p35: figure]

Finally, if you have any questions (as no doubt, I’ve probably forgotten a bunch of things), feel free to email me at:

rob.appleby@wildspy.com.au

All the best for your drop-off adventures!

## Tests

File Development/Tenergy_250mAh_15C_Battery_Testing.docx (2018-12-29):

The 250mAh, 15C, TEnergy battery was tested for compatibility with the NichDrop. The battery was discharged through a 1.73Ohm load over approx 9 minutes. The resulting discharge curve is shown in blue below.

Figure 1 - Discharge of the battery over a 1.73 Ohm load

The low battery voltages are due to the battery’s internal resistance. The red line is the battery’s source voltage. That is, the voltage measured over its terminals plus the voltage drop over its internal resistor. The value of this internal resistor was calculated to be 0.50 Ohms.

To determine the internal resistance the following method was used. First, the no-load battery voltage was measured. Then the battery was attached to a known load of 1.73 Ohms and the battery voltage was measured again. The internal resistance was calculated with the following formula:

R_s =(V_(NoLoad) -V_(Load) )/I_(Load)

Where ILoad is the current through the load and Rs is the internal battery resistance. Table 1 shows the results of this experiment.

Battery | Vnoload | Vload | Rload | I | Vir | Rs | Avg Rs
1 | 4.15 | 3.09 | 1.73 | 1.786127 | 1.06 | 0.520627
1 | 4.145 | 3.22 | 1.73 | 1.861272 | 0.925 | 0.496972
1 | 4.139 | 3.244 | 1.73 | 1.875145 | 0.895 | 0.477297
1 | 4.127 | 3.199 | 1.73 | 1.849133 | 0.928 | 0.501857
1 | 4.128 | 3.221 | 1.73 | 1.86185 | 0.907 | 0.48715 | 0.49678
2 | 4.18 | 3.3 | 1.73 | 1.907514 | 0.88 | 0.461333
2 | 4.165 | 3.327 | 1.73 | 1.923121 | 0.838 | 0.43575
2 | 4.16 | 3.307 | 1.73 | 1.911561 | 0.853 | 0.446232
2 | 4.15 | 3.283 | 1.73 | 1.897688 | 0.867 | 0.456872
2 | 4.152 Table 1 - Results from battery internal resistance calculations | 3.285 | 1.73 | 1.898844 | 0.867 | 0.456594 | 0.451356

Both batteries from the table were Single Cell 250mAh, 15C rated, Lithium Polymer batteries from TEnergy. The internal resistance taken to work with was the highest of the averages, 0.50 Ohms.

The critical voltage is the voltage below which the microprocessor will reset when the dropoff is activated. This voltage can be calculated using the formula below:

V_(crit) ≥V_(min) +I_(Nich) ×R_s

Where Vcrit is the critical battery voltage, Vmin is the microprocessor’s minimum operating voltage, INich is the current through the nichrome wire during the dropoff and Rs is the battery’s internal resistance. With Rs = 0.5Ω, Vmin = 2.0V and INich = 2.5A, the minimum value of Vcrit is 3.25V. This value is below the minimum battery voltage of 3.5V (for safe operation). Therefore, the value of Vcrit can be anything above 3.5V. Vcrit was chosen conservatively to be 3.6V and Vlow was chosen to be 3.7V.

Figure 2 - Discharge of the battery over a 1.73 Ohm load

From Figure 2 it can be determined that the useable energy in this battery is approximately 200mAh. This equates to 4 years and one month with an average sleep draw of 5 micro amps.

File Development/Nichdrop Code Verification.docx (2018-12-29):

# Testing

Verified | Function
| int main(void);
X | void SaveWakeupInfo(void);
X | void DropOff (void);
X | void Release(unsigned int);
X | void ShowMenu(void);
X | void RTCWakeup(void);
X | void RTCFullWakeup(void);
X | inline void WriteTimeEEPROM(struct RTCTime*, uint16_t);
X | inline void ReadTimeEEPROM(struct RTCTime*, uint16_t);
X | void ReadEEPROM(uint8_t*, uint8_t, uint16_t);
X | void WriteEEPROM(uint8_t*, uint8_t, uint16_t);
X | uint16_t GetBatVoltage(void);
X | void ADC_Setup(void);
X | uint16_t ADC_Read();
X | void ADC_Stop();
X | void BacktoSleep(uint8_t);
X | void PrintRTC(void);
X | static inline void delay_ms(uint16_t);
- | uint8_t Process_RX_Data(const uint32_t* , uint8_t );
- | uint8_t RX_RF_DATA(const uint32_t* , uint8_t* , uint8_t );
- | uint8_t TX_RF_DATA(const uint32_t* , uint8_t* , uint8_t );
X | void StartTim10ms(uint16_t);
X | void StopTim10ms(void);

# 1 General Functions

## 1.1 Main Function

Synopsis

int main(void);

Description/Reasoning | Input | Expected Output | Actual Output | Pass/Fail
Class 1 – Visual Code Inspection | | | | Pass
Class 2 –Practical Use Test | Code has been used | No Problems Caused | No Problems Caused | Pass

## 1.2 Record Wakeup Information Function

Synopsis

void SaveWakeupInfo(void);

Description/Reasoning | | Input | Expected Output | Actual Output | Pass/Fail
Class 1 – Repeated Entries
1.1 | Repeated entries | 255 Entries | No writing past end of EEPROM or before 0x51 | Started writing at 0x51 and stopped at 501 decimal (7 bytes written here so 501-508) Continued to increment the counter but no further writing to EEPROM. | Pass
Class 2 –Practical Use Test | | Code has been used | No Problems Caused | No Problems Caused | Pass

## 1.3 Start 10 Millisecond Timer Function

Synopsis

void StartTim10ms(uint16_t Time);

Description/Reasoning | Input | Expected Output | Actual Output | Pass/Fail
Class 2 –Practical Use Test | Code has been used | No Problems Caused | No Problems Caused | Pass

## 1.4 Stop 10 Millisecond Timer Function

Synopsis

void StopTim10ms(void);

Description/Reasoning | Input | Expected Output | Actual Output | Pass/Fail
Class 2 –Practical Use Test | Code has been used | No Problems Caused | No Problems Caused | Pass

## 1.5 Delay in Milliseconds Function

Synopsis

static inline void delay_ms(uint16_t ms);

Description/Reasoning | Input | Expected Output | Actual Output | Pass/Fail
Class 1 – Visual Code Inspection | | | | Pass
Class 2 –Practical Use Test | Code has been used | No Problems Caused | No Problems Caused | Pass

# 2 Core Functions

## 2.1 Short RTC Wakeup Function

Synopsis

void RTCWakeup(void);

Description/Reasoning | | Input | Expected Output | Actual Output | Pass/Fail
Class 1 – Triggers (no RF RX)
1.1 | Not yet wakeup time | Waketime < CurrentTime | Set Alarm for 10s, no full wakeup, No RF RX | Set Alarm for 10s, no full wakeup, No RF RX | Pass
1.2 | After wakeup time | Waketime > CurrentTime | Set Alarm for 10s, do full wakeup, No RF RX | Set Alarm for 10s, do full wakeup, No RF RX | Pass
Class 2 – Triggers (with RF RX)
2.1 | Not yet wakeup time | Waketime < CurrentTime | Set Alarm for 10s, no full wakeup, do RF RX and process | Set Alarm for 10s, no full wakeup, do RF RX and process | Pass
2.2 | After wakeup time | Waketime > CurrentTime | Set Alarm for 10s, do full wakeup, do RF RX and process | Set Alarm for 10s, do full wakeup, do RF RX and process | Pass

## 2.2 Full RTC Wakeup Function

Synopsis

void RTCFullWakeup(void);

Description/Reasoning | | Input | Expected Output | Actual Output | Pass/Fail
Class 1 - Normal
1.1 | Good Bat, Alarm > 1 day | As per description | Alarm set 1 day from now | Alarm set 1 day from now | Pass
1.2 | Good Bat, Alarm < 1 day | As per description | Alarm set to aTime | Alarm set to aTime | Pass
1.3 | Alarm Time Good Bat | As per description | Dropoff, set alarm for 1 min | Dropoff, set alarm for 1 min | Pass
1.4 | Low Bat, Alarm > 4 hrs | As per description | Alarm set 4 hrs from now | Alarm set 4 hrs from now | Pass
1.5 | Low Bat, Alarm < 4 hrs | As per description | Alarm set to aTime | Alarm set to aTime | Pass
1.6 | Alarm Time Low Bat | As per description | Dropoff, set alarm for 1 min | Dropoff, set alarm for 1 min | Pass
1.7 | Alarm Time Crit Bat | As per description | Dropoff, set alarm for 1 min | Dropoff, set alarm for 1 min | Pass
1.8 | Crit Bat | As per description | Dropoff, set alarm for 1 min | Dropoff, set alarm for 1 min | Pass
Class 2 -
| Invalid Alarm Time and Alarm Time | As per description | Alarm set to INVALID TIME! | Alarm set to INVALID TIME! | Not Good
| Invalid Alarm Time, Good Bat, Alarm < 1 day | As per description | Alarm set to INVALID TIME! | Alarm set to INVALID TIME! | Not Good
| Invalid Alarm Time and Crit Bat | As per description | Dropoff, set alarm for 1 min | Dropoff, set alarm for 1 min | Pass

Key things to note here is that invalid alarm times are NOT supported and will NOT be automatically fixed by the Nichdrop.

## 2.3 Drop Off Function

Synopsis

void DropOff (void);

Description/Reasoning | Input | Expected Output | Actual Output | Pass/Fail
Class 1 – Visual Code Inspection | | | | Pass

## 2.4 Release Function

Synopsis

void Release(unsigned int ms);

Description/Reasoning | Input | Expected Output | Actual Output | Pass/Fail
Class 1 – Validation from experience – has never failed in the many tests it’s been in | | | | Pass

## 2.5 Go Back to Sleep Function

Synopsis

void BacktoSleep(uint8_t skip_SleepMSG);

Description/Reasoning | Input | Expected Output | Actual Output | Pass/Fail
Class 1 – Visual Code Inspection | | | | Pass
Class 2 –Practical Use Test | Code has been used | No Problems Caused | No Problems Caused | Pass

# 3 USART Communication Functions

## 3.1 Show Menu Function

Synopsis

void ShowMenu(void);

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

## 3.2 Print RTC Function

Synopsis

void PrintRTC(void);

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

# 4 EEPROM Functions

## 4.1 Write Time to EEPROM Function

Synopsis

inline void WriteTimeEEPROM(struct RTCTime* mTime, uint16_t Address);

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

## 4.2 Read Time From EEPROM Function

Synopsis

inline void ReadTimeEEPROM(struct RTCTime* mTime, uint16_t Address);

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

## 4.3 General Read from EEPROM Function

Synopsis

void ReadEEPROM(uint8_t* Data, uint8_t Length, uint16_t Address);

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

## 4.4 General Write to EEPROM Function

Synopsis

void WriteEEPROM(uint8_t* Data, uint8_t Length, uint16_t Address);

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

# 5 ADC Functions

## 5.1 Get Battery Voltage Function

Synopsis

uint16_t GetBatVoltage(void);

Description/Reasoning | Input | Expected Output | Actual Output | Pass/Fail
Class 2 –Practical Use Test | Code has been used | No Problems Caused | No Problems Caused | Pass

## 5.2 Setup ADC Function

Synopsis

void ADC_Setup(void);

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

## 5.3 Take ADC Reading Function

Synopsis

uint16_t ADC_Read();

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

## 5.4 Disable ADC Function

Synopsis

void ADC_Stop();

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

# 7 RF Functions

## 7.1 Process Received RF Data Function

Synopsis

uint8_t Process_RX_Data(const uint32_t* part1, uint8_t AllowStayOn);

Description/Reasoning | | Input | Expected Output | Actual Output | Pass/Fail
Class 1 -
1.1
1.2
1.3
Class 2 -

Not Presently Verified

## 7.2 Receive RF Data Function

Synopsis

uint8_t RX_RF_DATA(const uint32_t* part1, uint8_t* DestData, uint8_t b_len);

Description/Reasoning | | Input | Expected Output | Actual Output | Pass/Fail
Class 1 -
1.1
1.2
1.3
Class 2 -

Not Presently Verified

## 7.3 Transmit RF Data Function

Synopsis

uint8_t TX_RF_DATA(const uint32_t* part1, uint8_t* SrcData, uint8_t b_len);

Description/Reasoning | | Input | Expected Output | Actual Output | Pass/Fail
Class 1 -
1.1
1.2
1.3
Class 2 -

Not Presently Verified

# 6 RTC Functions

## 6.1 Get Byte from RTC Function

Synopsis

unsigned char RTC_get(unsigned char pos);

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

## 6.2 Get Flags from RTC Function

Synopsis

unsigned char RTC_getflags(void);

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

## 6.3 Set Byte on RTC Function

Synopsis

void RTC_set(unsigned char pos, unsigned char val);

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

## 6.4 Set Byte on RTC with Mask Function

Synopsis

void RTC_set_msk(unsigned char pos, unsigned char val, unsigned char bMsk);

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

## 6.5 Enable RTC Alarm Function

Synopsis

void RTC_EnableAlarm(void);

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

## 6.6 Print Time to USART Function

Synopsis

void PrintTime(struct RTCTime*pTime , char* lbl);

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

## 6.7 Get RTC Time Function

Synopsis

void RTC_GetTime(struct RTCTime* Time);

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

## 6.8 Get RTC Alarm Function

Synopsis

void RTC_GetAlarm(struct RTCTime* Alarm);

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

## 6.9 Set RTC Time Function

Synopsis

void RTC_SetTime(struct RTCTime* Time);

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

## 6.10 Set RTC Alarm Function

Synopsis

void RTC_SetAlarm(struct RTCTime* Alarm);

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

## 6.11 Convert Integer to BCD Function

Synopsis

uint8_t IntToBCD(uint8_t val);

Description/Reasoning | | Input | Expected Output | Actual Output | Pass/Fail
Class 1 – Random Valid Inputs
1.1 | 9 | 09 | 0x09 | 0x09 | Pass
1.2 | 18 | 18 | 0x18 | 0x18 | Pass
1.3 | 27 | 27 | 0x27 | 0x27 | Pass
1.4 | 36 | 36 | 0x36 | 0x36 | Pass
1.5 | 45 | 45 | 0x45 | 0x45 | Pass
1.6 | 99 | 99 | 0x99 | 0x99 | Pass
1.7 | 0 | 0 | 0x00 | 0x00 | Pass
Class 2 –Erroneous Inputs
2.1 | 100 | 100 | 0x99 | 0x99 | Pass
2.2 | 123 | 123 | 0x99 | 0x99 | Pass
2.3 | 255 | 255 | 0x99 | 0x99 | Pass

## 6.12 Convert BCD to Integer Function

Synopsis

uint8_t BCDToInt(uint8_t val);

Description/Reasoning | | Input | Expected Output | Actual Output | Pass/Fail
Class 1 – Random Valid Inputs
1.1 | 0x09 | 0x09 | 9 | 9 | Pass
1.2 | 0x18 | 0x18 | 18 | 18 | Pass
1.3 | 0x27 | 0x27 | 27 | 27 | Pass
1.4 | 0x36 | 0x36 | 36 | 36 | Pass
1.5 | 0x45 | 0x45 | 45 | 45 | Pass
1.6 | 0x99 | 0x99 | 99 | 99 | Pass
1.7 | 0x00 | 0x00 | 0 | 0 | Pass
Class 2 –Erroneous Inputs
2.1 | 0xA0 | 0xA0 | 99 | 99 | Pass
2.2 | 0xFF | 0xFF | 99 | 99 | Pass
2.3 | 0xC4 | 0xC4 | 99 | 99 | Pass

## 6.13 Copy Time Function

Synopsis

void CopyTime (struct RTCTime* SrcTime, struct RTCTime* DstTime);

Description/Reasoning | | Input | Expected Output | Actual Output | Pass/Fail
Class 1 – Random Time/Date
1.1 | Now | 13:32:25 on 13/7/10 | 13:32:25 on 13/7/10 | 13:32:25 on 13/7/10 | Pass

## 6.14 Add Times Together Function

Synopsis

void AddTimes(struct RTCTime* DateTime, struct RTCTime* AddTime);

Description/Reasoning | | Input | Expected Output | Actual Output | Pass/Fail
Class 1 - Normal | | Input 1 = 10-10-10 10:10:10 | (Input 1)
1.1 | Add Second | Input 2 = 00-00-00 00:00:35 | 10-10-10 10:10:45 | 10-10-10 10:10:45 | Pass
1.2 | Add Minute | Input 2 = 00-00-00 00:24:00 | 10-10-10 10:34:10 | 10-10-10 10:34:10 | Pass
1.3 | Add Hour | Input 2 = 00-00-00 12:00:00 | 10-10-10 22:10:10 | 10-10-10 22:10:10 | Pass
1.4 | Add Day | Input 2 = 00-00-08 00:00:00 | 10-10-18 10:10:10 | 10-10-18 10:10:10 | Pass
1.5 | Add Month | Input 2 = 00-01-00 00:00:00 | 10-11-10 10:10:10 | 10-11-10 10:10:10 | Pass
1.6 | Add Year | Input 2 = 03-00-00 00:00:00 | 13-10-10 10:10:10 | 13-10-10 10:10:10 | Pass
1.7 | Add All | Input 2 = 03-01-08 12:24:35 | 13-11-18 22:34:45 | 13-11-18 22:34:45 | Pass
Class 3 – Basic Overflow | | Input 1 = 10-10-10 10:10:10 | (Input 1)
3.1 | Second Overflow | Input 2 = 00-00-00 00:00:55 | 10-10-10 10:11:05 | 10-10-10 10:11:05 | Pass
3.2 | Minute Overflow | Input 2 = 00-00-00 00:53:00 | 10-10-10 11:03:10 | 10-10-10 11:03:10 | Pass
3.3 | Hour Overflow | Input 2 = 00-00-00 18:00:00 | 10-10-11 04:10:10 | 10-10-11 04:10:10 | Pass
3.4 | Day Overflow | Input 2 = 00-00-25 00:00:00 | 10-11-04 10:10:10 | 10-11-04 10:10:10 | Pass
3.7 | Month Overflow | Input 2 = 00-05-00 00:00:00 | 11-03-10 10:10:10 | 11-03-10 10:10:10 | Pass
3.8 | All Overflow | Input 2 = 00-05-25 18:53:55 | 11-04-05 05:04:05 | 11-04-05 05:04:05 | Pass
Class 4 – Month Overflows | | Input 2 = 00-00-20 00:00:00 | (Input 1)
4.1 | 30 Day Month Overflow | Input 1 = 10-04-15 00:00:00 | 10-05-05 00:00:00 | 10-05-05 00:00:00 | Pass
4.2 | 31 Day Month Overflow | See 3.7 | See 3.7 | See 3.7 | Pass
4.3 | February Overflow Non Leap Year | Input 1 = 10-02-20 00:00:00 | 10-03-12 00:00:00 | 10-03-12 00:00:00 | Pass
4.4 | February Overflow Leap Year (%4) | Input 1 = 08-02-20 00:00:00 | 08-03-11 00:00:00 | 08-03-11 00:00:00 | Pass
| February Overflow Leap Year (%400) | Input 1 = 00-02-20 00:00:00 | 00-03-11 00:00:00 | 00-03-11 00:00:00 | Pass
| No Leap Year (%4 && %100) | Input 1 = 100-02-20 00:00:00 | 100-03-12 00:00:00 | 100-03-12 00:00:00 | Pass
Class 5 – Rolling Overflow | | Input 2 = 00-00-00 00:00:10 | (Input 1)
5.1 | Seconds Through To Year | Input 1 = 10-12-31 23:59:53 | 11-01-01 00:00:03 | 11-01-01 00:00:03 | Pass
Class 6 – Multiple Overflows | | Input 1 = 10-10-10 10:10:10 | (Input 1)
6.1 | Seconds | Input 2 = 00-00-00 00:00:200 | 10-10-10 10:13:30 | 10-10-10 10:13:30 | Pass
6.2 | Minutes | Input 2 = 00-00-00 00:200:00 | 10-10-10 13:30:10 | 10-10-10 13:30:10 | Pass
6.3 | Hours | Input 2 = 00-00-00 56:00:00 | 10-10-12 18:10:10 | 10-10-12 18:10:10 | Pass
6.4 | Days | Input 2 = 00-00-60 00:00:00 | 10-12-09 10:10:10 | 10-12-09 10:10:10 | Pass
6.5 | Months | Input 2 = 00-27-00 00:00:00 | 13-01-10 10:10:10 | 13-01-10 10:10:10 | Pass
6.6 | All | Input 2 = 00-27-60 56:200:200 | 13-03-11 21:33:30 | 13-03-11 21:33:30 | Pass

## 6.15 Clear Time Function

Synopsis

void ClearTime(struct RTCTime* Time1);

Description/Reasoning | | Input | Expected Output | Actual Output | Pass/Fail
Class 1 – Clearing Times
1.1 | Clear Random Time | 13:32:25 on 13/7/10 (13/7/2010) | 00:00:00 on 0/0/00 | 00:00:00 on 0/0/00 | Pass
1.2 | Clear Empty Time | 00:00:00 on 0/0/00 | 00:00:00 on 0/0/00 | 00:00:00 on 0/0/00 | Pass
Class 2 – Erroneous Inputs
2.1 | Pass Invalid Pointer | Invalid Pointer | Garbage/Corruption of data | Garbage/Corruption of data | Pass

## 6.16 First Time Greater Function

Synopsis

uint8_t CompareTimesGreater (struct RTCTime* Time1, struct RTCTime* Time2);

Description/Reasoning | | Input | Expected Output | Actual Output | Pass/Fail
Class 1 – Time1 < Time2 | | Time1 = 10-10-10 10:10:10
1.1 | Seconds Less Than | Time2 = 10-10-10 10:10:11 | 0 | 0 | Pass
1.2 | Minutes Less Than | Time2 = 10-10-10 10:11:10 | 0 | 0 | Pass
1.3 | Hours Less Than | Time2 = 10-10-10 11:10:10 | 0 | 0 | Pass
1.4 | Days Less Than | Time2 = 10-10-11 10:10:10 | 0 | 0 | Pass
1.5 | Months Less Than | Time2 = 10-11-10 10:10:10 | 0 | 0 | Pass
1.6 | Years Less Than | Time2 = 11-10-10 10:10:10 | 0 | 0 | Pass
1.7 | All Less Than | Time2 = 11-11-11 11:11:11 | 0 | 0 | Pass
Class 2 – Time 1 > Time 2 | | Time2 = 10-10-10 10:10:10
1.1 | Seconds Less Than | Time1 = 10-10-10 10:10:11 | 1 | 1 | Pass
1.2 | Minutes Less Than | Time1 = 10-10-10 10:11:10 | 1 | 1 | Pass
1.3 | Hours Less Than | Time1 = 10-10-10 11:10:10 | 1 | 1 | Pass
1.4 | Days Less Than | Time1 = 10-10-11 10:10:10 | 1 | 1 | Pass
1.5 | Months Less Than | Time1 = 10-11-10 10:10:10 | 1 | 1 | Pass
1.6 | Years Less Than | Time1 = 11-10-10 10:10:10 | 1 | 1 | Pass
1.7 | All Less Than | Time1 = 11-11-11 11:11:11 | 1 | 1 | Pass
Class 3 – Time 1 == Time 2 | | Time1 = 10-10-10 10:10:10
3.1 | Equal Times | Time2 = 10-10-10 10:10:10 | 2 | 2 | Pass

## 6.17 DateTime is Valid Function

Synopsis

uint8_t ValidDateTime(struct RTCTime* Time1);

Description/Reasoning | Input | Expected Output | Actual Output | Pass/Fail
Class 1 – Visual Inspection of Code | | | | Pass

## 6.18 Compare Times Function

Synopsis

uint8_t CompareTimes (struct RTCTime* Time1, struct RTCTime* Time2);

Description/Reasoning | Input | Expected Output | Actual Output | Pass/Fail
Class 1 - Visual Inspection of Code | | | | Pass

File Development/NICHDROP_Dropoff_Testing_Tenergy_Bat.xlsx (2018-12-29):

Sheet: Sheet1
Board | Test No. | Initial Vbat (avg) | Minimum Vbat | Min Vbat (Overshoot) |  | Drop Time (s) | TOP | RESET | Frequency (Hz) | Duty Cycle | Max Nichrome Current (A) | Battery Capacity (mAh) | Dicharge Current (C) | Micro Reset | Nicrome Heat | Pass/ Fail
Norm | 1 | 4.22 | 4.16 |  |  | 5 | 130 | 90 | 7692.307692 | 69.2% | ?? | 250 |  | No | RED HOT | PASS
Norm | 2 | 4.22 | ?? |  |  | 5 | 130 | 90 | 7692.307692 | 69.2% | 3.46 | 250 | 13.8 | No | RED HOT | PASS
Norm | 3 | 4.22 | 3.26 | 1.98 |  | 5 | 130 | 90 | 7692.307692 | 69.2% | 3.42 | 250 | 13.7 | No | RED HOT | PASS | 1.049079755
Norm | 4 | 4.20 | 3.26 | 2.20 |  | 5 | 130 | 90 | 7692.307692 | 69.2% | 3.58 | 250 | 14.3 | No | RED HOT | PASS | 1.098159509
Norm | 5 | 4.18 | 2.51 | 1.62 |  | 5 | 100 | 40 | 10000 | 40.0% | 3.07 | 250 | 12.3 | No | RED HOT | PASS | 1.22310757
Norm | 6 | 4.16 | 3.32 | 1.68 |  | 5 | 100 | 40 | 10000 | 40.0% | 3.06 | 250 | 12.2 | No | RED HOT | PASS | 0.921686747
Norm | 7 | 4.15 | 2.54 | 1.64 |  | 5 | 100 | 40 | 10000 | 40.0% | 3.06 | 250 | 12.2 | No | RED HOT | PASS | 1.204724409
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

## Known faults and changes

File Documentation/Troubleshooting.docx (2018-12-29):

# Troubleshooting: Nichdrop

# (Timer only version)

1. Symptom: Won’t Program, read weird device signature.

Date: 31/5/2011

Cause: ISP programming speed set too high.

Solution: Set ISP programming speed to 250kbps or less.

2. Symptom: Won’t Program, read device signature 0x000000

Date: 31/5/2011

Cause: Unknown.

Solution: Disconnect AVRISPMk2 from computer and reconnect.

3. Symptom: Won’t Program... Can’t connect to Programmer in Wild Spy Programmer

Date: 31/5/2011

Cause: Programmer connected elsewhere?

Solution: Close programming window in AVRStudio.

4. Symptom: RTC doesn’t tick. (Chip programmed correctly)

Date: 31/5/2011

Cause: Bad crystal.

Solution: Replace crystal.

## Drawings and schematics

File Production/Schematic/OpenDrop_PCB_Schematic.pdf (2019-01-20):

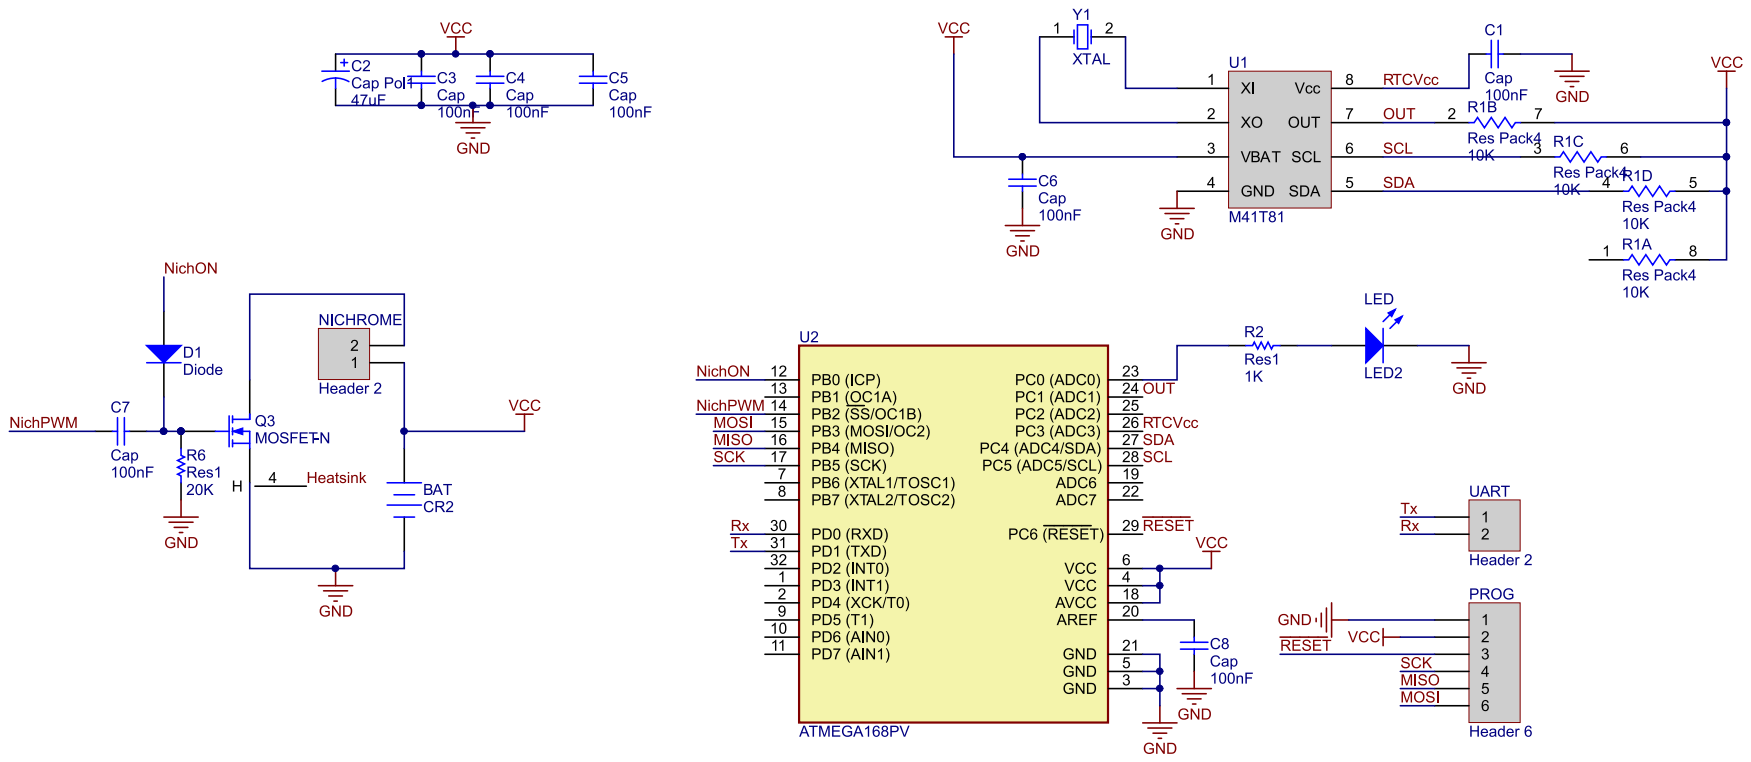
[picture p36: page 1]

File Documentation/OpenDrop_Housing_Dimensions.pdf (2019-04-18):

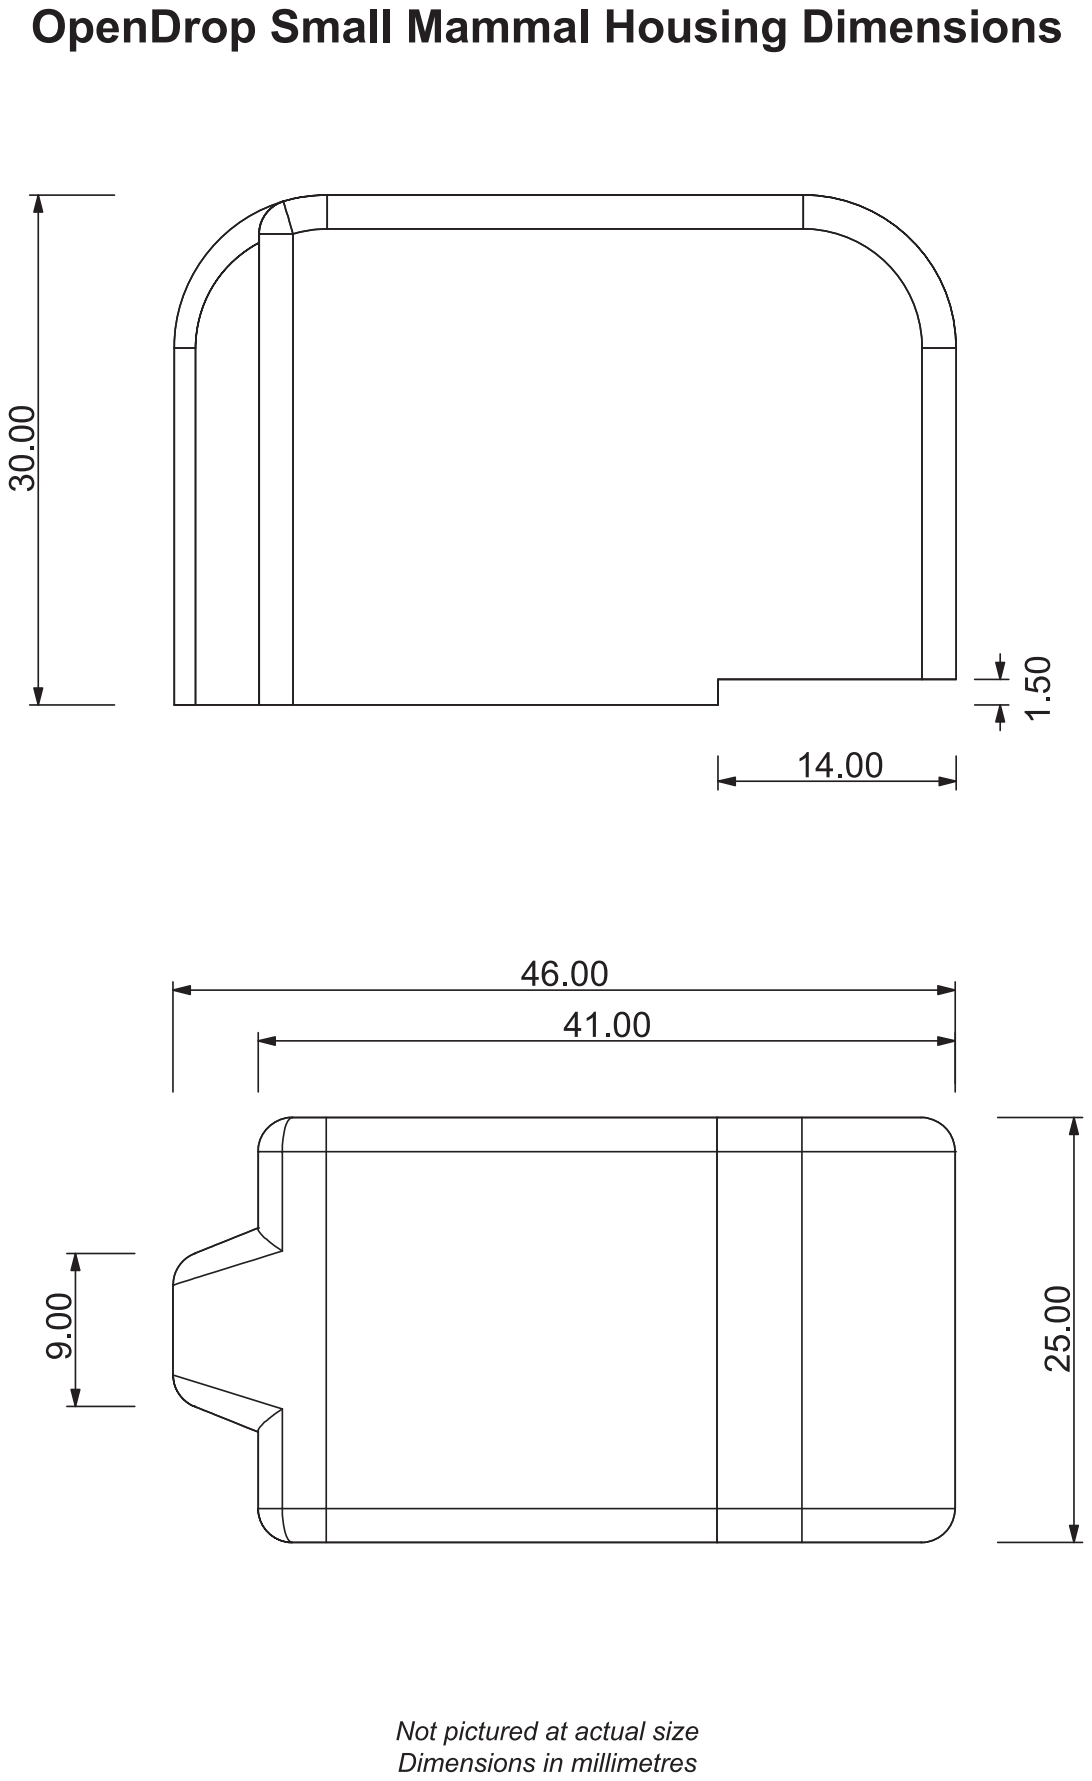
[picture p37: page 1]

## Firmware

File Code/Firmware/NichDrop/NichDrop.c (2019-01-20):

/*
 * NichDrop.c
 *
 *		  Name: MOSFET Trigged Timer Based Dropoff
 *  Created on: 03/02/2010
 *      Author: Matthew Cochrane
 *  	   MCU: ATMEGA168(PV)
 *   Fuse Bits:
 *   	High - 0xDF
 *   	 Low - 0x62
 *
 */

#include "NichDrop.h"

char s[80];
char s1[80];
volatile unsigned char patience;
uint8_t wakeSource = WAKEUP_SOURCE_NONE;
unsigned char ICRR;
unsigned char OCRR;
unsigned char DropTime;
unsigned char DevArmed;
unsigned char Wakeups;
unsigned char wtick;
uint32_t Device_ID;
RTC_Time_t aTime;
RTC_Time_t wTime;
unsigned char BGRefV[5];	//char 5 for '\0'
volatile uint16_t timer10ms = 0;
uint8_t WakeDecision = WAKEUP_ACT_WASRESET;

ISR(TIMER0_OVF_vect) {
	USART_UpdateTimers();
}

ISR(PCINT2_vect) {
	wakeSource = WAKEUP_SOURCE_UART;
}

ISR(PCINT1_vect) {
	wakeSource = WAKEUP_SOURCE_RTC;
}

int main(void) {

	RTC_Time_t mTime1, mTime2, mTime3;

	PCMSK1 |= (1<<PCINT9); 	// for the RTC alarm
	PCMSK2 |= (1<<PCINT16); // for RS232/UART

	//0 - LED, 3 - RTCVCC, 4 - SDA, 5 - SCL
	DDRC = (1<<0)|(1<<3)|(1<<4)|(1<<5);
	//USART Tx
	DDRD = (1<<1);
	//0 - NichON, 2 - NichPWM (Charge Pump)
	DDRB = (1<<2)|(1<<0);

	// Enable pullups
	PORTC = 0b00111001;
	PORTD = 0b11111111;

	//Load in values from EEPROM:
	ReadEEPROM(BGRefV, 4, CONVFACTADD);
	ReadEEPROM((uint8_t*)&Device_ID, 4, DEVIDADD);
	ReadEEPROM(&DevArmed, 1, DEVARMEDADD);
	ReadEEPROM(&DropTime, 1, DROPTIMEADD);
	ReadEEPROM(&OCRR, 1, TOPADD);
	ReadEEPROM(&ICRR, 1, RESETADD);
	ReadTimeEEPROM(&aTime, ALARMTADD);

	BGRefV[4] = '\0';

	if (!ValidDateTime(&aTime)) {
		ReadTimeEEPROM(&aTime, DALARMTADD);
	}

	if (DevArmed == ARM_SHELF) {
		RTCProgOn;
		//Enable the stop bit on the RTC
		RTC_set_msk(0x01,0, 0b10000000);
	} else {

		ReadTimeEEPROM(&mTime1, LASTWAKEADD);

		//If the RTC time is no longer valid then
		//set the RTC to the last time we woke up..
		//In case of a power failure.
		RTCProgOn;
		RTC_GetTime(&mTime2);

		//Generate a time 1 day after the last wakeup
		ClearTime(&mTime3);
		mTime3.Day = 1;
		mTime3.Hour = 1;
		AddTimes(&mTime3, &mTime1);

		if (ValidDateTime(&mTime2) && FirstTimeGreater(&mTime2,&mTime1) && !(FirstTimeGreater(&mTime2, &mTime3))) {
			//TODO[x]:  If the RTC time is set to some random garbage date on reset that happens to be valid
			//			and also after the last wakeup, we're in trouble.  Check to see that the RTC time is no
			//			more than one day after the last wakeup time (as it shouldn't be).
			//RTC Time is valid, after the last wakeup time but not by more than one day.
			//Leave the RTC time as is and set the last wakeup time to now.
			WriteTimeEEPROM(&mTime2, LASTWAKEADD);

			//wake up in 10 seconds
			ClearTime(&mTime3);
			mTime3.Second = 10;
			AddTimes(&mTime2, &mTime3);
			CopyTime(&mTime2,&wTime);
			RTC_SetAlarm(&mTime2);

			//make sure the timer is running
			if (RTC_get(0x01)&0b10000000)
				RTC_set_msk(0x01,0, 0b10000000);
		} else {
			if (!ValidDateTime(&mTime1)) {
				//For initial time after programming.. or if time becomes invalid
				ReadTimeEEPROM(&mTime1, DTIMEADD);
				//stop the timer
				RTC_set_msk(0x01,0b10000000, 0b10000000);
			} else {
				//Time is valid
				//wake up in 3 seconds
				RTC_SetTime(&mTime1);
				ClearTime(&mTime2);
				mTime2.Second = 3;
				AddTimes(&mTime1, &mTime2);
				CopyTime(&mTime1,&wTime);
				RTC_SetAlarm(&mTime1);
			}
		}
	}

	//enable interrupts
	sei();

	set_sleep_mode(SLEEP_MODE_PWR_DOWN);
	_delay_ms(1000);
	BacktoSleep(1);

	while (1) {

		if (wakeSource == WAKEUP_SOURCE_UART) {
			PORTC |= (1<<0); // turn on LED
			PCICR &=~((1<<PCIE2));//|(1<<PCIE1)); // Disable  interrupts
			PRR &= ~((1<<PRUSART0)|(1<<PRTWI)|(1<<PRSPI)); // Turn ON the USART, TWI and SPI

			//Setup USART for 9600bps
			USART_Setup(UBRRVAL,1);

			_delay_ms(10);
			Wakeups++;
			//sprintf_P(s1, PSTR("Waking up... (%d)\r\n"),Wakeups);
			//USART_tx_String(s1);
			//while ( UCSR0A & (1<<RXC0)) wtick = UDR0;
			//USART_tx_String_P(PSTR("UART woke me up\r\n"));

			RTCProgOn;

			//Handle serial comms
			do {
				while ( UCSR0A & (1<<RXC0)) wtick = UDR0;
			} while (Ser_CMDHandler() != SerCom_err_Timeout);

			if (DevArmed == ARM_SHELF) {
				//Enable the RTC Stop Bit
				RTC_set_msk(0x01,0b10000000, 0b10000000);
			} else {
				//Just in case we were interrupted by the RTC while awake (i.e. we missed that RTC
				//wake up), run through all the RTCWakeup code.  If we missed one and we don't do this
				//the RTC will never wake us up again and we'll be stuck asleep forever!
				RTCFullWakeup();
			}
			BacktoSleep(0);

		} else if (wakeSource==WAKEUP_SOURCE_RTC) {
			if (DevArmed == ARM_SHELF) {
				RTCProgOn;
				//Enable the RTC Stop Bit
				RTC_set_msk(0x01,0b10000000, 0b10000000);
			} else {
				RTCFullWakeup();
				BacktoSleep(0);
			}
		} else
			BacktoSleep(1);
	}

	return 0;
}

void SetNextWakeupIn(uint8_t months, uint8_t days, uint8_t hrs, uint8_t mins, uint8_t secs) {
	RTC_Time_t mTime1, mTime2;
	
	RTC_GetTime(&mTime1);
	ClearTime(&mTime2);
	mTime2.Month = months;
	mTime2.Day = days;
	mTime2.Hour = hrs;
	mTime2.Minute = mins;
	mTime2.Second = secs;
	AddTimes(&mTime1,&mTime2);
	CopyTime(&mTime1, &wTime);
	RTC_SetAlarm(&wTime);
}

#ifdef DEBUGWAKESAVE
void SaveWakeupInfo() {
	//First just save the time...
	//First byte is no. of entries.
	RTC_Time_t mTime1;
	uint8_t mIndex;
	uint16_t EEPAdd;

	if (DevArmed == ARM_SHELF)
		return;

	//if we didn't dropoff then don't save any info.
	if (WakeDecision != WAKEUP_ACT_NONE || wakeSource == WAKEUP_SOURCE_UART) {
		mIndex = eeprom_read_byte((uint8_t*)RECENTRIES);

		EEPAdd = RECSTART+7*mIndex;

		if (EEPAdd >= RECSTART && EEPAdd < 506) {

			PRR &= ~((1<<PRTWI)); // Turn ON the TWI
			//Setup I2C (TWI)
			RTCProgOn;
			//Get the current RTC time
			RTC_GetTime(&mTime1);

			WriteTimeEEPROM(&mTime1, EEPAdd);
			eeprom_write_byte((uint8_t*)(EEPAdd+6), WakeDecision | wakeSource<<4);
			//increment the index:
			eeprom_write_byte((uint8_t*)RECENTRIES, mIndex + 1);
		}
	}
}
#endif


void DropOff () {
	uint16_t tmpDropTime = ((unsigned int)eeprom_read_byte((uint8_t*)DROPTIMEADD))*1000;
	PORTC |= (1<<0);
	uint8_t Acts;
	Acts = eeprom_read_byte((uint8_t*)ACTIVATIONS);
	if (Acts < 6) {
		if (DevArmed == ARM_ON) {
			//Device is armed - DROPOFF!!!
			Release(tmpDropTime);
		} else {
			delay_ms(tmpDropTime);
		}
		eeprom_write_byte((uint8_t*)ACTIVATIONS, Acts + 1);
	}
}

void Release ( unsigned int ms ) {

	unsigned char step = 0;

	ICRR = eeprom_read_byte((uint8_t*)TOPADD);
	OCRR = eeprom_read_byte((uint8_t*)RESETADD);

	step = (ICRR-OCRR)/10;

	OCRR = ICRR;

	PRR &= ~(1<<PRTIM1);		//enable Timer1
	ICR1 = ICRR;				//count to ??
	OCR1BL = OCRR;   			//duty ratio = ??
	OCR1BH = 0;
	TCNT1 = 0;

	PORTB |= (1<<0);			//enable the charge pump
	TCCR1A = 0b11110000;		//Setting up Timer 1
	//TCCR1B = 0b00010001;		//f = fCPU
	TCCR1B = 0b00010010;		//f = fCPU/8 - 1MHz

	delay_ms(ms);

	TCCR1A = 0;					//Turn off the timer
	PRR |= (1<<PRTIM1);			//disbale the timer
	PORTB &= ~(1<<0);			//Turn off the charge pump
	delay_ms(1);
}

//void ShowMenu () {
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

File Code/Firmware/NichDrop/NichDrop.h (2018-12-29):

/*
 * NichDrop.h
 *
 *  Created on: 03/02/2010
 *      Author: Matthew Cochrane
 */

#ifndef NICHDROP_H_
#define NICHDROP_H_

//Includes
#include <stdio.h>
#include <stdlib.h>
#include <string.h>
#include <avr/io.h>
#include <avr/eeprom.h>
#include <avr/interrupt.h>
#include <avr/sleep.h>
#include <avr/wdt.h>
#include <util/delay.h>
#include "Libs/M_RTC.h"
#include "Libs/M_USART.h"
#include "Libs/MX_SerComms.h"
#include "Strings.h"

//Define
#define CPU8MHZ 1
#define DEBUGWAKESAVE 1
//#define CPU1MHZ 1
#ifdef CPU8MHZ
	#define UBRRVAL 		0x0067 	//for 8MHz (Double Speed)
	#define TIMEOUT			16		//approx 500ms			//253		//aprox 8 seconds
	#define NORWAITTIMPRE 	(1<<CS02)
	#define NORWAITTIMOCA 	0x4E
	#define T0WAIT10MSOCA	0x4D
#endif
#ifdef CPU1MHZ
	#define UBRRVAL 		0x000C //for 1MHz (Double Speed)
	#define TIMEOUT			32	//aprox 8 seconds
	#define NORWAITTIMPRE 	(1<<CS01)|(1<<CS00)
	#define NORWAITTIMOCA 	0x26
	#define T0WAIT10MSOCA	0x13
#endif

#define WAKEUP_SOURCE_NONE 0
#define WAKEUP_SOURCE_UART 1
#define WAKEUP_SOURCE_RTC 2
#define WAKEUP_ACT_NONE 0
#define WAKEUP_ACT_RIGHTTIMEDROP 1	//correct time dropoff
#define WAKEUP_ACT_CRITVOLTDROP 2
#define WAKEUP_ACT_WASRESET 3
#define WAKEUP_ACT_RFRX 4
#define WAKEUP_ACT_RFDROP 5
#define WAKEUP_ACT_USARTTESTDROP 6

#define DEVIDADD	0x00	//a 4-byte integer (uint32_t)
#define TOPADD 		0x04	//a 1-byte integer (uint8_t)
#define RESETADD 	0x05	//a 1-byte integer (uint8_t)
#define DROPTIMEADD 0x06	//a 1-byte integer (uint8_t)
#define DEVARMEDADD	0x07	//a 1-byte integer (uint8_t)
#define RFVERSION	0x08	//a 1-byte integer (uint8_t)
#define ACTIVATIONS 0x09	//a 1-byte integer (uint8_t)
#define BATLOWADD	0x10	//a 2-byte integer	(uint16_t)
#define BATCRITADD	0x12	//a 2-byte integer	(uint16_t)
#define CONVFACTADD	0x14	//a 4-byte string	(unsigned char[4])
#define RFIDADD		0x20	//a 5-byte unsigned integer	(uint8_t[5])
#define RFCHANADD	0x25	//a 1-byte unsigned integer	(uint8_t)
#define LASTWAKEADD	0x30	//a 6-byte structure (struct RTCTime)
#define ALARMTADD	0x36	//a 6-byte structure (struct RTCTime)
#define DALARMTADD	0x3C	//a 6-byte structure (struct RTCTime)
#define DTIMEADD	0x42	//a 6-byte structure (struct RTCTime)

#define RECENTRIES	0x50	//a byte
#define RECSTART	0x51	//an array of 6 byte structs

#define ARM_OFF 	0
#define ARM_ON		1
#define ARM_DEBUG	2
#define ARM_SHELF	3

//Macros
#define NORM_WAKE_PERIOD_TO_ADD mTime2.Day = 1
//#define NORM_WAKE_PERIOD_TO_ADD mTime2.Second = 20
#define LOWBAT_WAKE_PERIOD_TO_ADD mTime2.Hour = 4
//#define LOWBAT_WAKE_PERIOD_TO_ADD mTime2.Second = 5

#define NichromeOn PORB |= (1<<0)
#define NichromeOff PORTB &= ~(1<<0)
#define PWMOn PORTB |= (1<<2)
#define PWMOff PORTB &= ~(1<<2)
#define ByteNO(SrcPtr, byteNo)	*(((uint8_t*)SrcPtr)+byteNo)

//Function Prototypes
//void ChargePumpCal(void);
void SaveWakeupInfo(void);
void DropOff (void);
void Release(unsigned int);
void ShowMenu(void);
void RTCFullWakeup(void);
void BacktoSleep(uint8_t);
uint16_t GetBatVoltage(void);
void ADC_Setup(void);
uint16_t ADC_Read();
void ADC_Stop();
void PrintRTC(void);
static void delay_ms(uint16_t);
void WriteTimeEEPROM(RTC_Time_t*, uint16_t);
void ReadTimeEEPROM(RTC_Time_t*, uint16_t);
void ReadEEPROM(uint8_t*, uint8_t, uint16_t);
void WriteEEPROM(uint8_t*, uint8_t, uint16_t);
void SetNextWakeupIn(uint8_t months, uint8_t days, uint8_t hrs, uint8_t mins, uint8_t secs);


#endif /* NICHDROP_H_ */

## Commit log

2018-12-29 Initial Commit - move into git from SVN
    [NICHDROP_Dropoff_Testing_Tenergy_Bat.xlsx, Nichrome Calcs.xlsx, NichromeDrop_V2R0.GBL, NichromeDrop_V2R0.GBO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]
2019-01-20 Added mould master CAD files
    [OpenDrop_Mould_Master.stl, OpenDrop_Mould_Master.stp]
2019-01-20 Added PCB schematic
2019-04-18 Added technical drawing for mould master
2019-04-18 Added BOM
    [OpenDrop_BOM.xls]
2023-03-11 Removed old PCB photos
2023-03-11 Added updated PCB photos
2023-11-06 Added remote drop-off assembly guide
2024-09-20 Added missing solder paste masks
    [NichromeDrop_V2R0.GBP, NichromeDrop_V2R0.GTP]
